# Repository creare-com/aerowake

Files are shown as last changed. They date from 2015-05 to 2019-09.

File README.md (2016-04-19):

# Aerowake

Also known as Wake Swarm, this is a project to measure air currents using a multicopter carrying an air pressure probe.

This repository hosts software to control the multicopter and its base station.

This project is a collaboration between Creare LLC and MIT.  For more information, please contact Creare and ask for Ben Cameron.  Contact information can be found [here](http://www.creare.com/about/contact.html).

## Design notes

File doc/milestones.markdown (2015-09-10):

# Software/Autopilot Mission Planning

---

## 1. System is integrated and demonstrated
In this milestone, the ground-control-pixhawk-raspberry pi-tether system is integrated and demonstrated on a real system. 

### Tasks
#### 1. Select the system configuration

~~In this task the initial hardware and interfaces are selected~~

#### 2. Integrate systems

In this task (Due 2015/9/17)

* ~~the raspberry pi can send/receive commands to/from the pixhawk at the maximum rate (10 Hz)~~
* ~~the raspberry pi can send/receive commands to/from the ground station~~
* ~~the ground station can receive telemetry/GPS information from the pixhawk~~
* the ground station can send GPS information and mission commands to the raspberry pi, and receive data packages from from the raspberry pi
* ~~the pixhawk can receive commands from the raspberry pi and send gps/telemetry information to the raspberry pi~~
* ~~the pixhawk can send telemetry/gps information to the ground station~~

#### 3. Develop autonomous mission control

In this task (Due 2015/9/24)

* A user can specify a sampling grid with various parameters
   * ~~r, $\theta$, $\phi$, maxes and mins and number of points between max and min~~
   * loiter time at points
   * travel speed between points
* The sampling grid waypoints will be generated
* The raspberry pi can take this grid and control the pixhawk to cover the gridded area flying relative to the ground-station gps coordinates
* If communication with the ground station is lost, the raspberry pi can interrupt the mission and control the pixhawk to land
   * Same thing with other critical problems (Such as low battery) -- need to define failure criteria

#### 4. Manual System Demonstration

In this task (Due 2015/09/24), it will be demonstrated that the copter can fly when manually controlled when

* the copter is untethered and the ground station is stationary
* the copter is tethered and the ground station is stationary
* the copter is tethered and the ground station is moving

#### 5. Autonomous System Demonstration

In this task (Due 2015/10/08), it will be demonstrated that the copter can fly a simple grid pattern relative to the ground station when

* the copter is untethered and the ground station is stationary
* the copter is untethered and the ground station is moving
* the copter is tethered and the ground station is stationary
* the copter is tethered and the ground station is moving

#### 6. Tether reel integration
In this task (Due 2015/10/15)

* The reel control can be controlled through the ground station
* The reel status can be sent to the raspberry pi, and the raspberry pi can ask the ground control station to reel the copter in or out
* In case of catastrophe, the reel will automatically retract to pull the copter back to landing

-----
## 2. System is optimized and stable
In this milestone, the copter-tether dynamical system is understood from energy-optimal and stability perspectives, and can be robustly controlled. 

### Tasks

#### 1. Analytically analyze the tether-copter system to determine limits of the performance envelope
In this task (Due 2015/11/10)

* Equation for the tether-copter system are developed
* The maximum tether-copter angles (both $\theta$ and $\phi$ are calculated to show where the tether reduces energy requirements

#### 2. Optimize energy performance
In this task (Due 2015/11/10)
* A function or lookup table for the optimal tether tension and copter pitch is calculated (inputs being tether length, $\theta$, and $\phi$

#### 3. Optimize stability
In this task (Due 2015/11/10)

* The best tether attachment point is determined

---
## 3. Ground Control Software is user-friendly
In this milestone, then Ground control software has an easy-to-use and robust GUI

### Tasks
#### 1. Integrate outputs received from quadcopter with GUI elements in GCS
~~In this task (Due 2015/09/17) there are new dials to show the outputs from measurements in real time~~

#### 2. Add custom mission control buttons
In this task (Due 2015/09/17), new GUI elements are added to control the mission on a high level. This includes specifying the grid, controlling the tether, ~starting and stopping the mission, emergency landing, and emergency stop~

#### 3. Validate and test GUI components with Hardware for normal usage
In this task (Due 2015/10/01), it is verified that the GUI buttons and outputs work as expected

#### 4. Test GUI elements

In this task (Due 2015/10/15), it is verified that the GUI buttons and outputs work as expected for anticipated emergency cases

----
# Other Milestones

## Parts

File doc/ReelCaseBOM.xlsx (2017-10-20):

Reel Case BOM |  | Up to date as of: | 2017-10-17
 | Brand | Part/Model # | QTY | Notes
Flight Electronics
Single-board computer |  | Raspberry Pi 3 | 1
915MHz Radio | 3DR | Pixhawk Radio Set, 915 mhz | 1
Pixhawk | 3DR | Pixhawk | 1
GPS module | 3DR |  | 1
Buzzer | 3DR |  | 1
I2C A to D converter | Adafruit | ADS1115 | 1
Power Supplies
5-12-24 Power supply | Traco Power | 495-TXL-100-0534TI | 1
48V Power supply | TKD-LAMBDA | SWS300 | 1
Case Hardware
Switch /Port mount | Digikey/Creare | HM577 HAMMOND BOX
Power switch | McMaster | 8002K82 | 1
Antenna port | Digikey | ACX1244 SMA BULKHEAD | 2
Antenna adapter | Digikey | ACX1248 SMA RPSMA SOCKET | 1
Antenna adapter | Digikey | ACX1247 SMA RPSMA SOCKET | 1
Antenna cable | Digikey | ACX1589 SMA 12" CABLE | 2
Antenna cap | Mouser | 523-8018-6174 SMA CAP | 2
Power port | Mouser | 654-MS3112E12-3P CONNECT | 1
Power cord | Digikey | MS3116F-12-35-MIL CONN | 1
Power port cap | Digikey | 1591-1044-MIL 12-3 CAP | 1
USB port | Digikey | APC 1103 USB HEADER | 1
USB port cap | Digikey | APC 1112 USB CAP | 1
USB plug | Digikey | APC 1107 USB PLUG | 1
Ethernet port | alliedelec | 70026494 AMP RJFTV21N | 1
Ethernet port cap | alliedelec | 70026506 AMP RJFTVC2N | 1
Ethernet plug | alliedelec | 70026500 AMP RJFTV6MN | 1
Exhaust fan | Sunon | GF92251B-000U-AE9 | 1
light green | McMaster | 2779K12 | 1
light blue | McMaster | 2779K2 | 1
Fuse Holder | McMaster | 7055K28 | 1
Tether pass-thru | McMaster/Creare
ANGULAR-CONTACT BALL BRNG | McMaster | 8828T216 | 1
THROUGH-WALL FITTING | McMaster | 36895K144 | 1
FOOD-GRADE DRY-RUNNING SLEEVE BRNG | McMaster | 57785K229 | 1
Motor/Reel Electronics
Motor controller | MAXON | 375711 EPOS2 70/10 | 1
Tension sensor | ELECTROMATIC | RFS150E/0200/08/3/O/4-20 | 1 | 0-200N range
Tether Encoder (Optical) | BAUMER (WALKER) | G1342A 227123 | 1
Gear/Motor/Encoder | MAXON | 136212 | 1 | 250W
Motor/Reel Mechanicals
Short Pulley Assy | Creare | 6614-010-0021 | 1
Long Pulley Assy | Creare | 6614-010-0022 | 1
Tensioner Assy | Creare | 6614-010-0030 | 1
6in Pulley | McMaster | 6245K480 | 1
Pillow Block Bearing | McMaster | 5913K610 | 2
Torque Limiter | McMaster | 6609K11 | 1 | 25 in-lbs
80/20 Frame | Creare | Custom | 1
Case
iM2620 STORM TRAK CASE | Pelican | iM2620 | 1

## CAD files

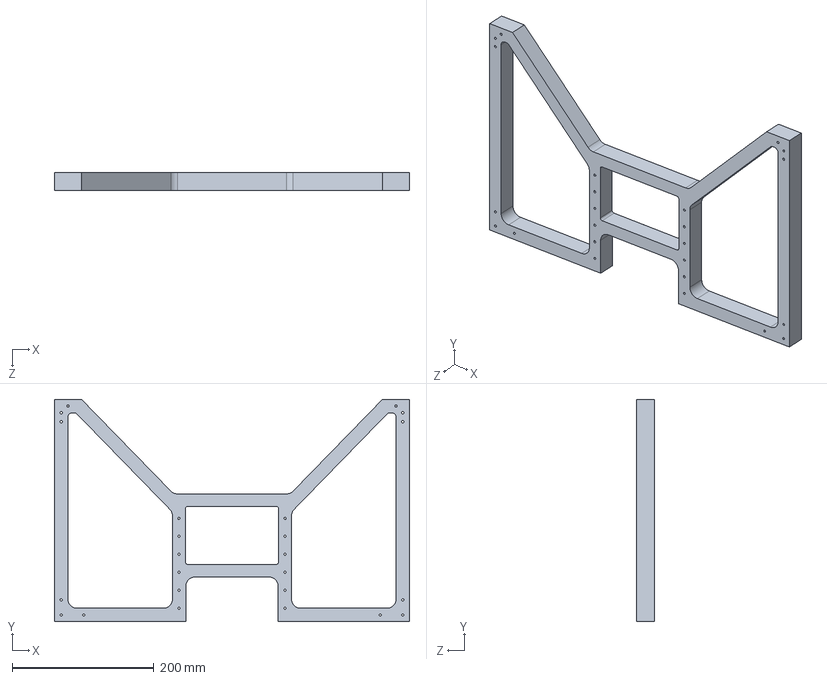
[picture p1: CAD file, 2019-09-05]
doc/design/1006614-002-0110 - Body Frame_rA.STEP
501.7 x 314.3 x 25.4 mm

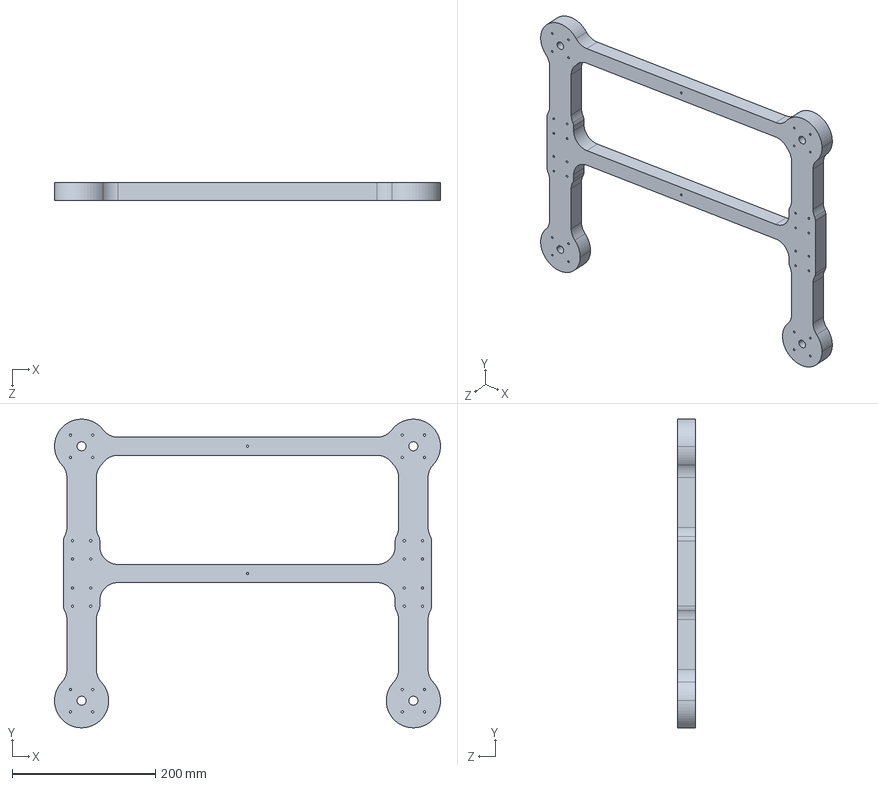
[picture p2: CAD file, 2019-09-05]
doc/design/1006614-002-0113 - Motor Mount Frame_rA.STEP
539.3 x 431.3 x 25.4 mm

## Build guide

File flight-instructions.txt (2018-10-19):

SIMPLE EXPLANATION IN ORDER

SSH into each device:
ssh odroid@192.168.1.3
ssh pi@192.168.1.6

Calibrate each pixhawk:

ODROID:
mavproxy.py --master=/dev/pixhawk,57600
accelcal
magcal start
magcal accept

RPi:
mavproxy.py --master=/dev/ttyAMA0,115200
accelcal
magcal start
magcal accept

Power cycle each pixhawk

Start flight commands:

ODROID:
sudo chmod a+rwx /dev/i2c-4
preflight.sh FILENAME

RPi:
ssg
ipython aerowake/Flight\ source/gcs/main.py FILENAME

Check on airprobe:

ODROID:
"CTRL+A,D" to detach from flight-cmd screen
"sral" to reattach to airprobe listener

Start rosbag (saving video)

ODROID:
"CTRL+A,D" to detach from airprobe listener
"ssb" to start bag screen
"rosbag record -a -x /camera/image --split --size=3000 --lz4 -o FILENAME" to start recording

Stop rosbag

ODROID:
"CTRL+C" in bag screen

Stop flight commands

ODROID:
postflight.sh

RPi:
End main.py with quit or CTRL+C

Playback rosbag

ODROID with monitor attached:
"CTRL+ALT+T" to start a terminal
roscore
"CTRL+SHIFT+O" to start a new terminal below the original
rosbag play /crearedrive/rosbag/FILENAME*
"CTRL+SHIFT+E" to start a new terminal next to the rosbag terminal
rosrun image_view image_view image:=/camera/image_raw

Logfile Storage Locations

airprobe log file: /crearedrive/airprobe-logs/FILENAME-TIME.log
uav main log file: /crearedrive/uav-logs/FILENAME-uav-TIME.log
rosbag log file: /crearedrive/rosbags/FILENAME
gcs main log file: /home/pi/logs/gcs-logs/FILENAME-gcs-TIME.log
gcs reel log file: /home/pi/logs/reel-logs/FILENAME-reel-TIME.log

################################################################################################################################################################################################################################################################################################################################################################################################################################################################################################

MORE COMPLETE EXPLANATIONS

SSH Connections

If unsure what IP address a device is on, log onto routerlogin.com (username: admin password: password) to see attached devices. IP addresses below are assigned to the WiFi chip itself, not the device. If you change WiFi chips, you will likely have a different IP from what is below.

RPi: 192.168.1.6
Yellow Hex: 192.168.1.3
FA39: 192.168.1.5

Initial Calibration

Need to calibrate camera on the drone. With the monitor attached, start roscore in one terminal, then launch the calibration method in a different terminal. Move the calibration target (extras in big MIT bin inside blue bag inside file box) around in the image until "Calibrate" lights up. Then click calibrate. It will likely take a few minutes until "Save" and "Commit" light up. Click "Save" followed by "Commit". The calibration file is created in ~/creare_ws/src/creare/params/camera_calib.yaml, even if the calibration terminal shows an error. 

roscore
<new terminal>
roslaunch creare calibrate.launch
<move calibration target in image>
<click calibrate>
<click save>
<click commit>
<CTRL+C launch terminal and roscore terminal>

Need to calibrate accelerometers and magnetometers on both pixhawks. When logged into each device below, issue the following commands to start MAVProxy, and then to begin calibration.

RPi:
mavproxy.py --master=/dev/ttyAMA0,115200

ODROID:
mavproxy.py --master=/dev/pixhawk,57600

In MAVProxy:

accelcal
Start accelcal, then follow prompts. If is hangs (doesn't go through all the prompts) and you try again and it always says calibrated, power cycle the pixhawk and complete accelcal through all of the prompts (end with "on its back"). 

magcal start
magcal accept
Start magcal, turn around in circles until it beeps confirmation, then accept once it says finished.

Pre- and Post-Flight Commands

Need to issue a number of commands in different screens (persistent SSH terminals) on the ODROID and RPi. 

ODROID:
preflight.sh FILENAME
<After flight, detach from flight-cmd screen with CTRL+A,D>
postflight.sh

I wrote shortcuts (stored in ~/creare_ws/src/aerowake/aerowake_git/preflight.sh and postflight.sh) to do so. 

The preflight shortcut will:
- start roscore in a detached screen
- start camera in a detached screen
- start flight companion in a detached screen
- start airprobe logging in a detached screen
- start airprobe checking (tail -f) in a detached screen
- reattach flight companion screen to view uav/main.py status

The postflight shortcut will:
- issue CTRL+C in all screens
- terminate all screens

RPi:
ssg
cd aerowake/Flight\ source/gcs
ipython main.py FILENAME

General Screen Commands

screen -ls
Lists all active screens.
screen -S NAME
Starts a screen with the given name.
screen -D NAME
Detaches from screen of given name.
CTRL+A,D
Detaches from current screen. Useful when a process is running on a screen and you can't type "screen -D NAME". If you press this combination in a terminal that is not a screen, it will close the terminal. 
screen -r NAME
Reattaches to screen of given name. A screen with that name must exist. 
killall screen
Terminates all active screens.

I wrote numerous shortcuts on the ODROID and RPi to quickly issue screen commands. See these commands in ~/creare_ws/src/aerowake/aerowake_git/.bash_aliases. The most useful ones are:

sls
Equivalent to "screen -ls".
skl
Equivalent to "killall screen".
srr
Equivalent to "screen -r roscore"
sry
Equivalent to "screen -r yaw-cmd". yaw-cmd is the camera start screen.
srf
Equivalent to "screen -r flight-cmd". flight-cmd is the flight companion screen.
sra
Equivalent to "screen -r airprobe". 
sral
Equivalent to "screen -r probe-check". probe-check is the "tail -f" screen.

Each ODROID Preflight Command Separately in Order

ssr (or "screen -S roscore")
roscore
CTRL+A,D
Start the roscore screen, start roscore, detach

ssy (or "screen -S yaw-cmd")
roslaunch creare yaw_commanding.launch
CTRL+A,D
Start the camera screen, start the camera, detach

ssf (or "screen -S flight-cmd")
roslaunch aerowake flight_companion.launch
CTRL+A,D
Start flight companion screen, start flight companion, detach

ssa (or "screen -S airprobe")
nice -n -10 ipython ~/creare_ws/src/aerowake/aerowake_git/Flight\ source/uav/airprobe/airprobe_main.py FILENAME
CTRL+A,D
Start airprobe screen, start airprobe with given filename, detach

ssal (or "screen -S probe-check")
tail -f /crearedrive/airprobe-logs/FILENAME*
CTRL+A,D
Start probe-check screen, echo live update tail of log file to screen, detach

srf (or "screen -r flight-cmd")
Reattach to flight-cmd screen to view uav/main.py status

Common Problems

If the airprobe won't start, you may not have set the i2c permissions. 
sudo chmod a+rwx /dev/i2c-4

Most other problems occur because you don't have the crearedrive plugged in, or the crearedrive you have plugged in doesn't have the correct directories. Each crearedrive automatically mounts to /crearedrive. Each crearedrive needs the following directories:
/crearedrive/airprobe-logs
/crearedrive/camera
/crearedrive/rosbags
/crearedrive/uav-logs

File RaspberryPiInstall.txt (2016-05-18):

Raspberry Pi Installation Guide
=================================
=================================

This can be slightly different depending on which Raspberry Pi (2 or 3). Differences should be noted. 

Setup of Raspberry Pi
=====================
-Install Basic Raspian via NOOBS (follow any online tutorial -- I am using NOOBS v1.4.1)
	-While it is installing, select Language = English (US) and Keyboard = (us)
-Default login is (pi), password is (raspberry)
-Notes:
	-To start the Raspberry Pi desktop, type $ startx
	-From the desktop, there is a wifi utility 
	- '$ [command]' will be terminal commands in this document
-Enter Raspberry Pi Config -- This often pops up when you first boot the RaspPi after installing the operating system. 
	$ sudo raspi-config
-Select '8. Advanced Options' and change:
	-A1 Overscan = Disable
	-A4 SSH = Enable
	-A7 I2C = Enable
	-A8 Serial = Disable
-Select Finish, reboot. 
-Setup Internet on the Raspberry Pi. (follow any online tutorial)
	-I used Wifi TP-Link WN722N, however there is a whole list of adapters recommended for the Raspberry Pi.
	-Ethernet should work fine. 
-Update the Raspberry Pi Software
	$ sudo apt-get update 
	$ sudo apt-get upgrade 
	$ sudo apt-get install git

Installation of Github Repository
====================================	
-Clone the repository
	$ git clone https:/github.com/creare-com/aerowake
	-This will probably require an authorized account. 

Serial Communication using GPIO pins
====================================
 -Run serial_enable_rasppi.sh in the aerowake repository
 	$ sudo ./serial_enable_rasppi.sh
 -The following can be used to change the baudrate, but are not necessary. 
 	for RaspPi 3:
 	$ sudo stty -F /dev/ttyS0 115200 
 	for RaspPi 2:
 	$ sudo stty -F /dev/ttyAMA0 115200

Installation of Dronekit and Mavproxy
=====================================
-Install packages 
	$ sudo apt-get install screen python-wxgtk2.8 python-matplotlib python-opencv python-pip python-numpy python-dev python-serial python-pyparsing 
	$ sudo pip install pymavlink
	$ sudo pip install mavproxy
	$ sudo ppip install dronekit

Testing of Pixhawk Connections
=====================================
	
-Use Mavproxy to ensure the pixhawk connections work. Start with the GCS pixhawk. Plug the Pixhawk Telemetry Radio into the Raspberry Pi. Set up the telemetry radios using a normal computer with Mission Planner, and confirm they work. 
	-Power the GCS Pixhawk on. 
	-Enter the following command  
	$ mavproxy.py --master=/dev/ttyUSB0 --baudrate 57600
	-You should see it initialize and say the firmware version**
	-When mavproxy is running, there are a list of commands that you can enter -- view all by typing help
	-For this document, Mavproxy commands will be shown as MAV> [command], however MAV will be the flight mode the vehicle is in, such as AUTO or MANUAL or ALTHOLD. 
	-If the pixhawk does not connect, there is an issue with the telemetry radio system. Most likely the issue is with the telemetry radios not being on the same channel. 
-Ctrl-C to exit Mavproxy. 
-Next attempt to connect to the UAV pixhawk.
 	-Ensure that the raspberry pi's GPIO pins are connected to the pixhawk's telemetry 1 port, and that the pixhawk is configured to use 115200 baud on that telemetry port. This is parameter SERIAL1_BAUD, and will have to be set using Mission Planner on a normal computer. 
 	-For the Raspberry Pi 2:
	$ mavproxy.py --master=/dev/ttyAMA0 --baudrate 115200
 	-For the Raspberry Pi 3:
 	$ mavproxy.py --master=/dev/ttyS0 --baudrate 115200
 	-If mavproxy cannot connect, it is most likely an issue with the Raspberry Pi's serial port on the GPIO. This can have to do with incorrect baud rates, the user not being on the dialout group, or the raspberry pi configuring the serial port for another function upon startup. The serial_enable_rasppi.sh script will hopefully fix these problems, but the Raspbery Pi 3 is known to be problematic with the serial port on the GPIO. 

Wiring Instructions
===================
-The Raspberry Pi 2 needs 5 volts @ up to 1A. Realistic current draw is ~.5A, but USB devices will draw more, so a large safety margin is good. 
	-I used 3 7805 5v Linear regulators in parallel (they got hot during operation)
	-Would recommend a high-power, high quality switching regulator such as this: http://www.amazon.com/Castle-Creations-Bec-Switching-Regulator/dp/B000MXAR12
	-This should be fed from a 12volt power source (3 cell LiPo) onboard the UAV. This battery hot-swappable, as we dont want to keep shutting down the raspberry pi.

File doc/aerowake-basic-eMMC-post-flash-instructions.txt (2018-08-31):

#---------------
# Setup Steps After Flashing aerowakebasic Image (Send questions to draper@mit.edu)
#---------------

Initially the ODROID will not boot due to having no hard disk space. To get it to boot, complete the following:

1. Press CTRL + ALT + F1 to enter a terminal
2. Login by typing odroid as the login and then again as the password
3. Start the ODROID Utility by typing "sudo odroid-utility.sh"
4. Within ODROID Utility, complete "4 Resize your root partition"
5. Within ODROID Utility, complete "7 Change Hostname", and change the hostname as desired -- DO NOT USE UNDERSCORES IN HOSTNAME
6. Once completed, reboot the ODROID using "sudo reboot now"

Once the ODROID boots to the desktop, complete the following:

1. Ensure you are connected to the internet
2. Start ODROID UTILITY again, and select "2 Update your Kernel/Firmware" then complete "1 Update Kernel"
3. Reboot using "sudo reboot now"
4. Then issue the following commands in order:
sudo apt-get update && sudo apt-get upgrade
cd ~/creare_ws/src
git clone https://Brndn004@bitbucket.org/Brndn004/creare.git
catkin_create_package aerowake
cd ~/creare_ws
catkin_make
cd ~/creare_ws/src/aerowake
git clone https://github.com/creare-com/aerowake.git aerowake_git
cd aerowake_git
git checkout may-2018-flight-testing
cd ~/creare_ws
catkin_make
sudo ln -s ~/creare_ws/src/aerowake/aerowake_git/Flight\ source/FA39.rules /etc/udev/rules.d/
sudo udevadm control --reload-rules && sudo udevadm trigger
git config --global user.email "Your Email"
git config --global user.name "Your Name"
mkdir ~/.ros/aerowake-logs
sudo reboot now

#---------------
# Programs Installed on this Installation Different from Base Ubuntu Image 
#---------------

- ROS Indigo
- ROS image_view package for when monitor attached to odroid
- ROS Catkin Workspace in ~/creare_ws/
- ROS Pointgrey Camera Driver built from source in ~/creare_ws/src/
- terminator (CTRL + ALT + T to open)
- pip
- Dronekit
- MAVProxy

#---------------
# Exact steps taken to set up this installation for Creare Aerowake
#---------------

<set system to allow updates from main, universe, restricted, and multiverse)
sudo apt-get update && sudo apt-get upgrade
sudo apt-get install terminator
<install ros by following directions at wiki.ros.org/indigo/installation/Ubuntu>
<set up catkin workspace in the ~/creare_ws/ directory by following directions at wiki.ros.org/ROS/Tutorials/InstallingandConfiguringROSEnvironment#Create_a_ROS_Workspace>
sudo apt-get install ros-indigo-image-view
sudo apt-get install python-rosinstall
cd ~/creare_ws/src
git clone https://github.com/ros-drivers/pointgrey_camera_driver.git
rosdep install --from-paths /path/to/your/catkin_ws/src --ignore-src
cd ~/creare_ws
catkin_make
<create /etc/udev/rules.d/40-pgr-custom.rules and paste inside:>
	SUBSYSTEM=="usb", ATTRS{idVendor}=="1e10", ATTRS{idProduct}=="3300", GROUP=="plugdev", SYMLINK+="firefly", MODE:="0666"
sudo service udev restart
sudo apt-get install libtcmalloc-minimal4
echo "export LD_PRELOAD=\"/usr/lib/libtcmalloc_minimal.so.4\"" >> ~/.bashrc
sudo apt-get install python-pip
sudo pip install dronekit
sudo pip install MAVProxy
sudo nano /usr/local/lib/python2.7/dist-packages/dronekit/__init__.py
<search for "timeout = kwargs" and change value from 30 to 180>
<change hostname in ODROID Utility -- DO NOT USE UNDERSCORES>
sudo reboot now

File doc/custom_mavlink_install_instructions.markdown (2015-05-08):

# Installing custom MAVLINK message to be used by the GCS and Raspberry pi
These custom messages are specified at the bottom of the: third_party/mavlink/pymavlink/dialects/v10/gcs_pixhawk.xml file

## Removing existing pymavlink installations
From commandline issue
```bash
sudo pip uninstall pymavlink
``` 

## Installing pymavlink from source
From commandline issue the following commands:
```bash
cd ~
cd aerowake-mit/third_party/mavlink/pymavlink
sudo python setup.py install
```

## Editing the messages
Simply edit the file mentioned above with new message or parameters, and then re-run `setup.py install`

## Notes
* This custom version of pymavlink has to be installed on both the GCS and the onboard PI to work
   * Hence why I included it in the repository
   * I also kept the .git folder so that we could potentially pull upstream changes (bugfixes) from the pymavlink project
* If you don't want to wait for all the mavlink protocols to be built use: 
```bash
sudo su
export NOGEN=0
setup.py install
exit
```

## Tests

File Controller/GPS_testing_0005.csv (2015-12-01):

log N | timestamp | roll | pitch | yaw | throttle | vox | voy | voz | vth | vphi | vr | airspd | lat | lon | alt | th | phi | goal_th | goal_phi | fx | fy | fz | fix | fiy | fiz | p | r | thr | yw | s_lat | s_lon | t_dist | s_alt | s_head | s_vel_x | s_vel_y | s_vel_z | v_rel_x | v_rel_y
1 | 15:09:44 | -0.01484086 | -0.06830316 | 52.36049314 | 1.23000000 | -0.47000000 | -0.39000000 | 0.47000000 | -0.53849802 | 0.47000000 | -0.28813170 | 0.00000000 | 1.00000000 | 1.00000000 | 0.00000000 | 138.46424372 | 0.00000000 | 0.00000000 | 20.00000000 | -3.74271029 | 3.31543658 | 20.94435000 | 3.28138291 | 3.70426798 | 0.71479013 | 1486.00000000 | 1300.00000000 | 1227.00000000 | 1537.00000000 | 42.35854040 | -71.09724260 | 8471102.97667107 | 0.00000000 | 60.00000000 | 0.00000000 | 0.00000000 | 0.00000000 | 0.57274991 | 0.21203194
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

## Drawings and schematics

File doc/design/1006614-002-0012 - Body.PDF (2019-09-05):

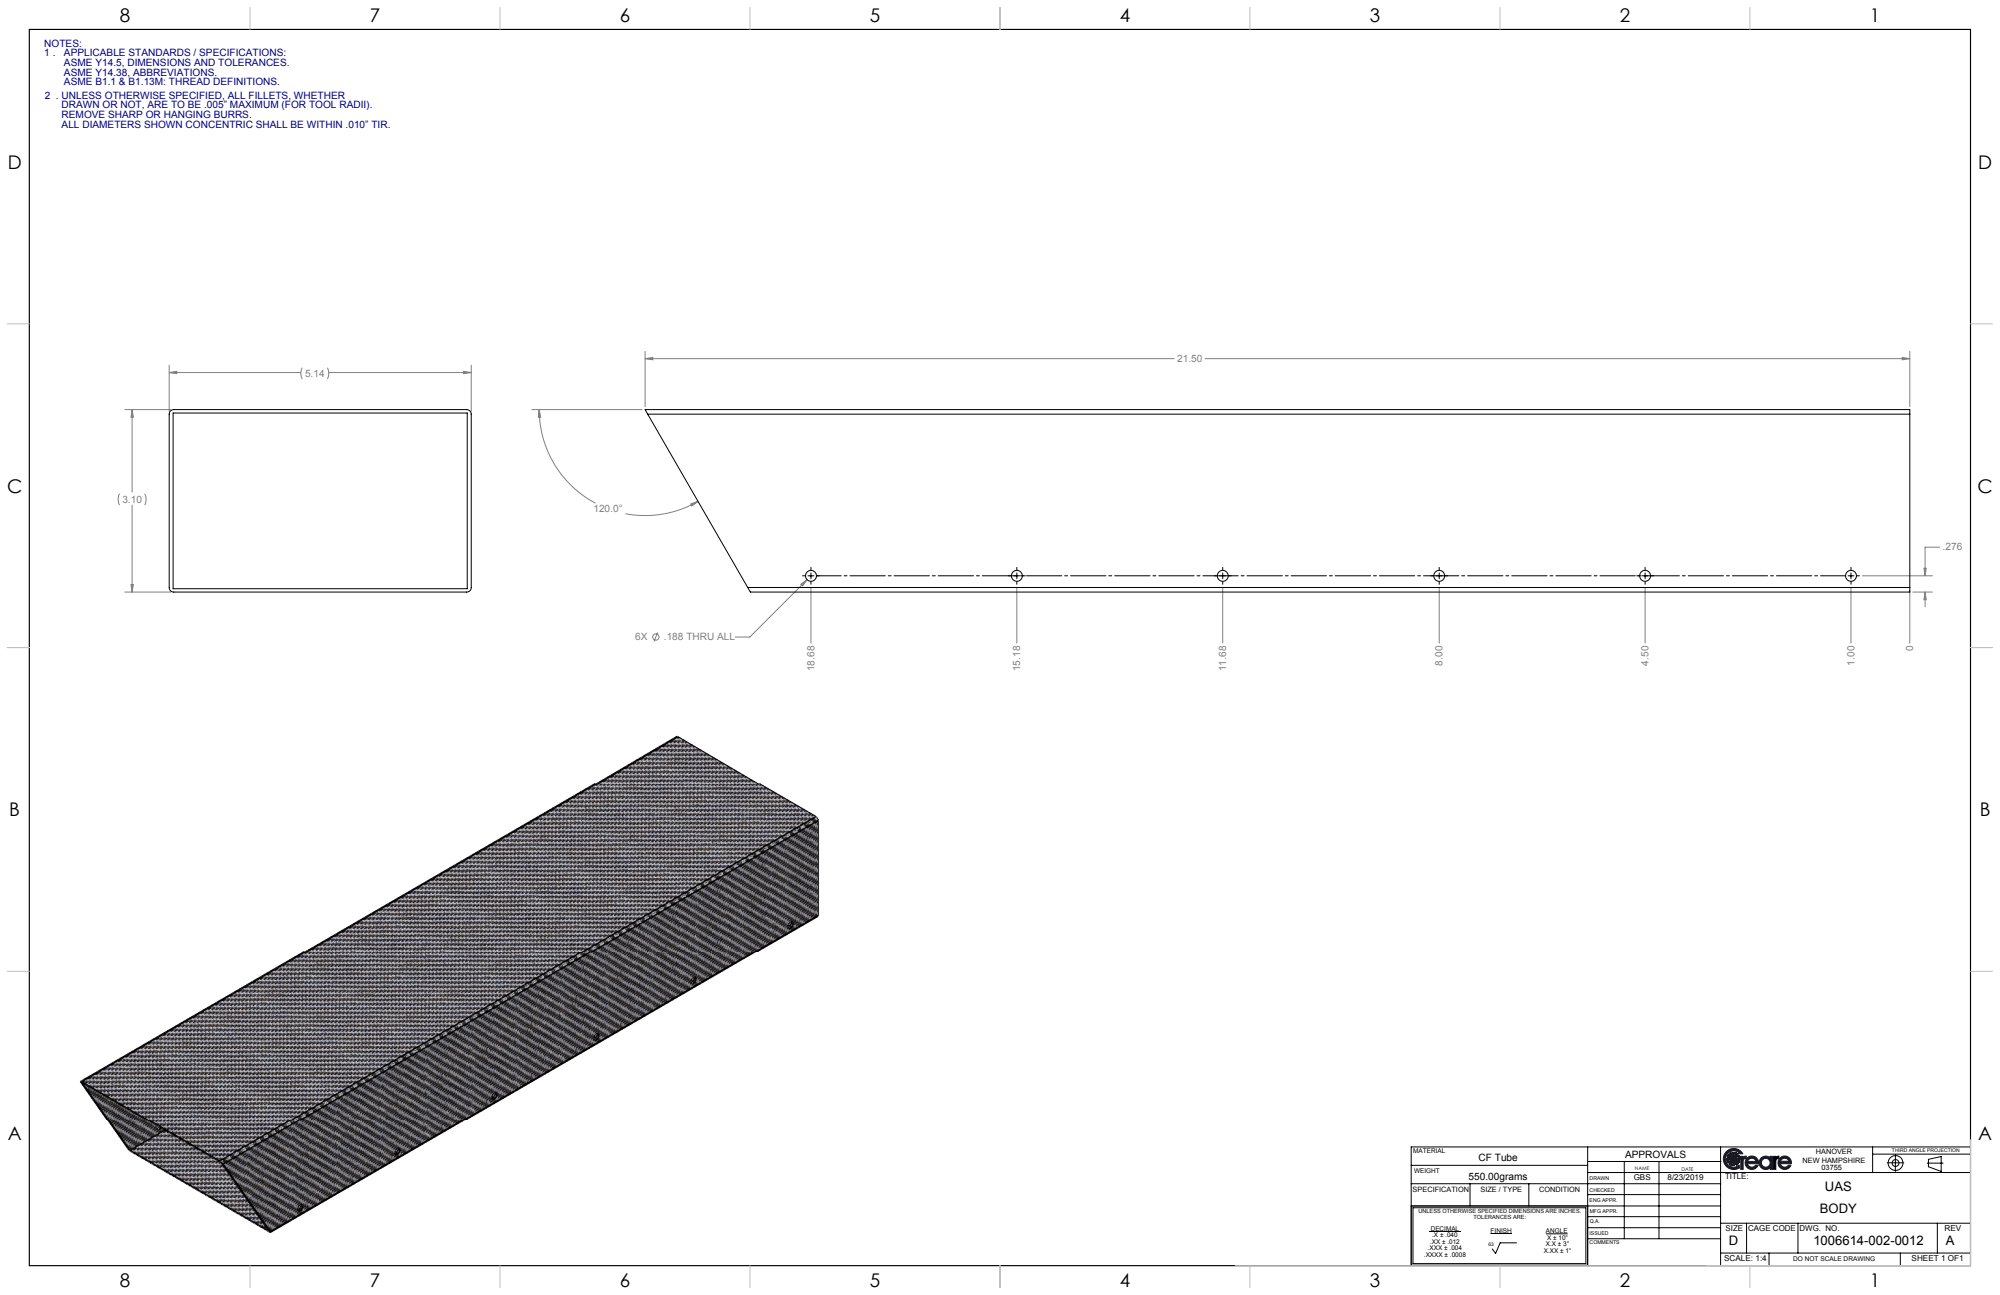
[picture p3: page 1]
TOLERANCES ARE:; .X ± .040 .XX ± .012 .XXX ± .004 .XXXX ± .0008; .188 THRU ALL; CF Tube; SCALE: 1:4; SHEET 1 OF1; SPECIFICATION SIZE / TYPE; CONDITION; NEW HAMPSHIRE APPROVALS; HANOVER; CAGE CODE; ENG APPR.; MFG APPR.; SIZE; DWG. NO.

NOTES:
1 . APPLICABLE STANDARDS / SPECIFICATIONS:
ASME Y14.5, DIMENSIONS AND TOLERANCES.
ASME Y14.38, ABBREVIATIONS.
ASME B1.1 & B1.13M: THREAD DEFINITIONS.
2 . UNLESS OTHERWISE SPECIFIED, ALL FILLETS, WHETHER
DRAWN OR NOT, ARE TO BE .005” MAXIMUM (FOR TOOL RADII).
REMOVE SHARP OR HANGING BURRS.
ALL DIAMETERS SHOWN CONCENTRIC SHALL BE WITHIN .010” TIR.

THIRD ANGLE PROJECTION

UNLESS OTHERWISE SPECIFIED DIMENSIONS ARE INCHES.

DO NOT SCALE DRAWING

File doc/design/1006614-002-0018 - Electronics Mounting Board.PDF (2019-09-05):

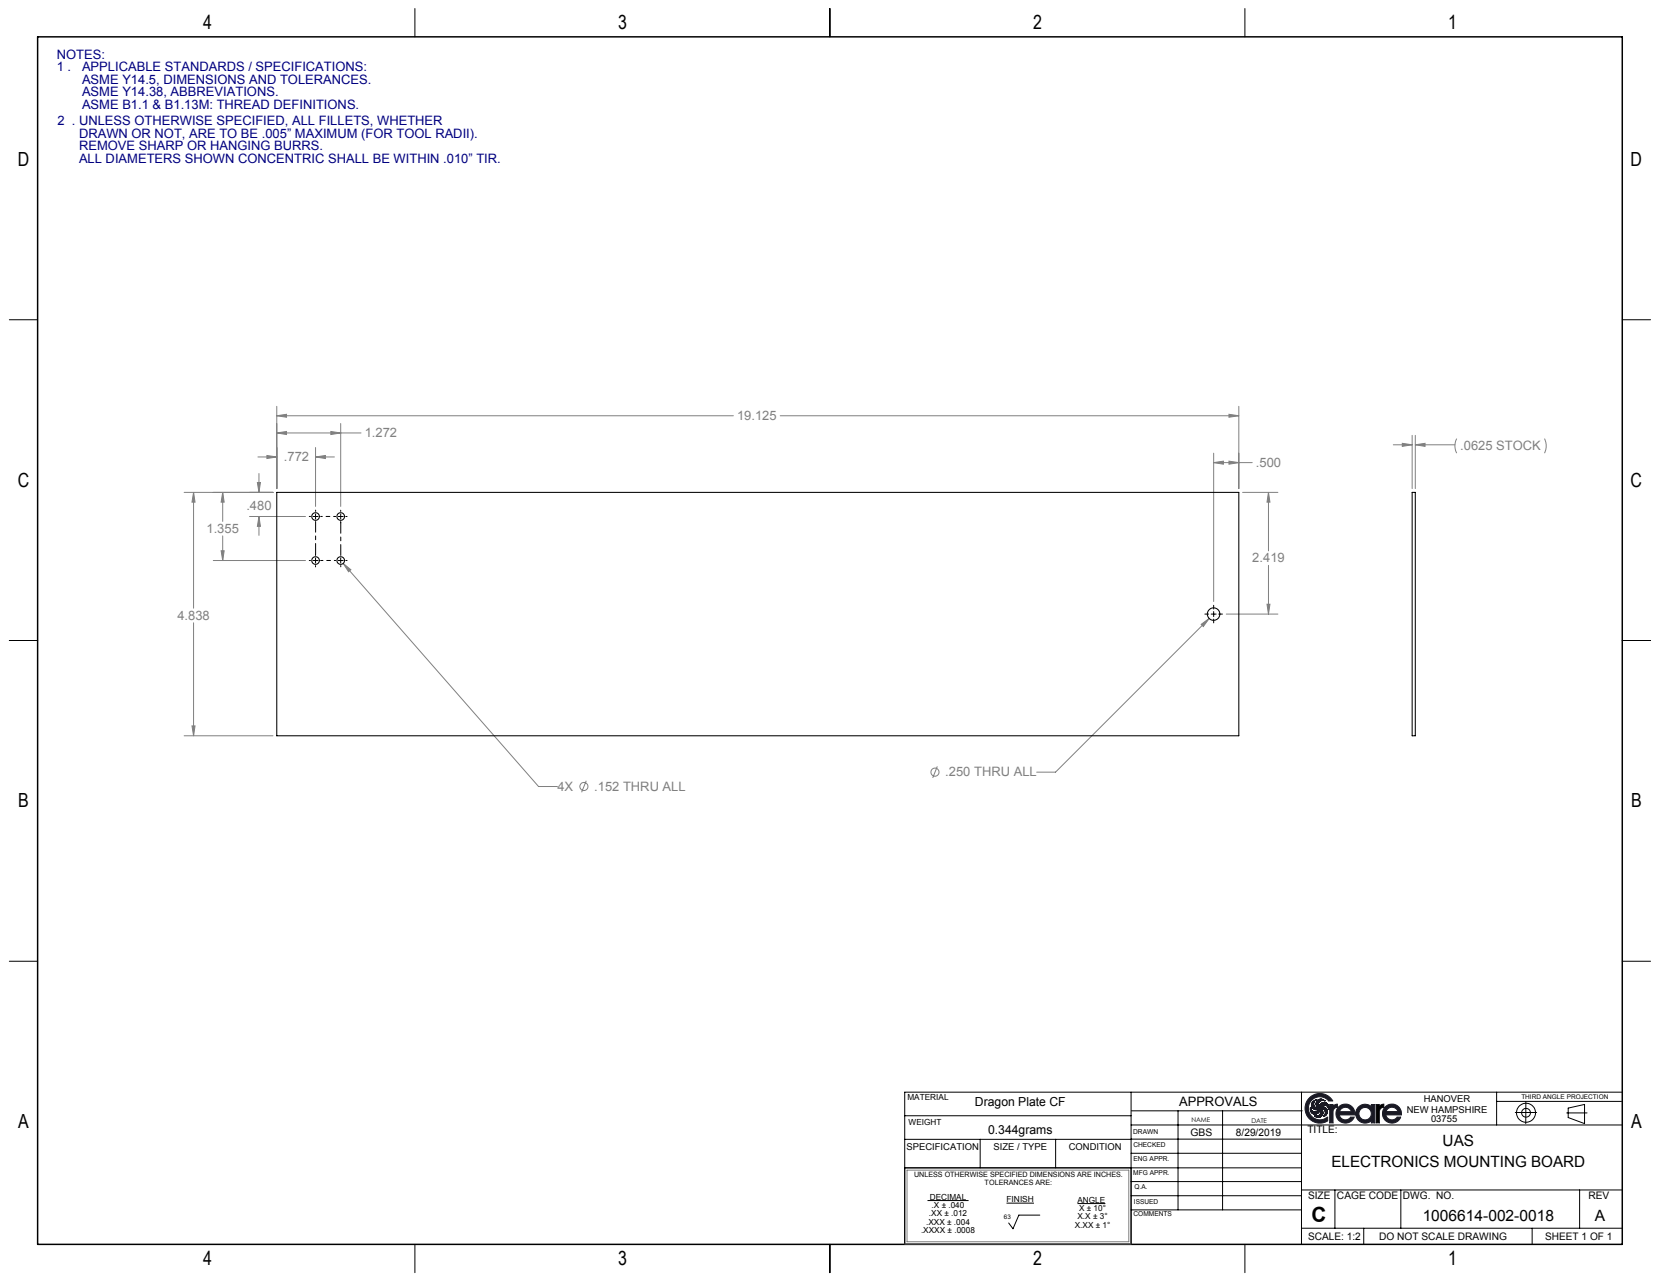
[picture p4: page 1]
TOLERANCES ARE:; .X ± .040 .XX ± .012 .XXX ± .004 .XXXX ± .0008; .152 THRU ALL; .250 THRU ALL; .0625 STOCK; ELECTRONICS MOUNTING BOARD; DO NOT SCALE DRAWING; SHEET 1 OF 1; SCALE: 1:2; DWG. NO.; REV; MFG APPR.; ENG APPR.; CAGE CODE; NEW HAMPSHIRE; SPECIFICATION SIZE / TYPE; CONDITION; UAS

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

ALL DIAMETERS SHOWN CONCENTRIC SHALL BE WITHIN .010” TIR.

THIRD ANGLE PROJECTION

Dragon Plate CF
0.344grams

UNLESS OTHERWISE SPECIFIED DIMENSIONS ARE INCHES.

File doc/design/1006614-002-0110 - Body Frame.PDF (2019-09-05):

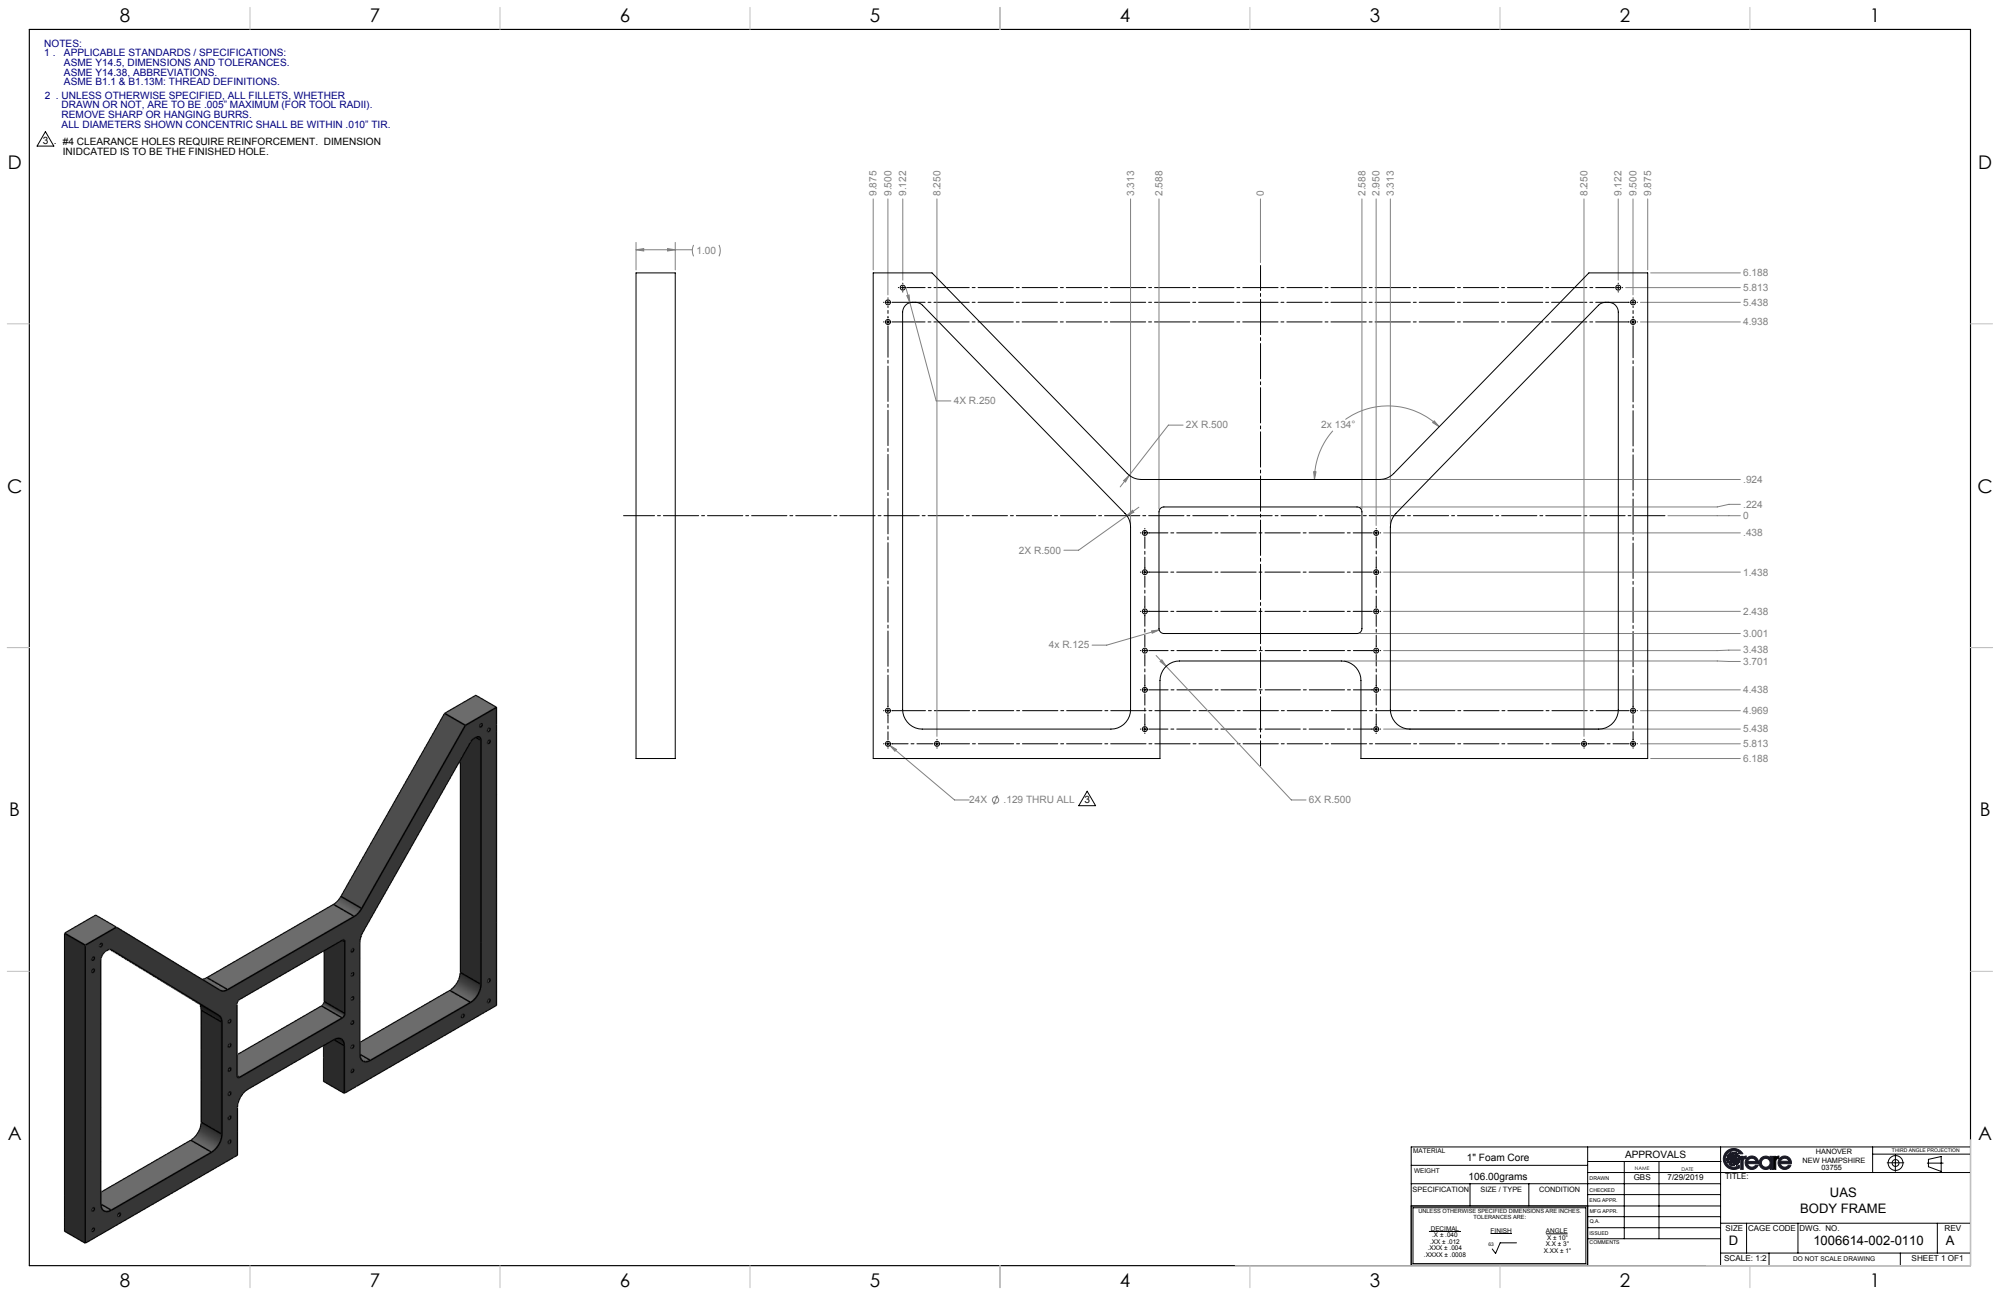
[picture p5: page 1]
TOLERANCES ARE:; .X ± .040 .XX ± .012 .XXX ± .004 .XXXX ± .0008; .129 THRU ALL; 1" Foam Core; SCALE: 1:2; SHEET 1 OF1; SPECIFICATION SIZE / TYPE; CONDITION; NEW HAMPSHIRE APPROVALS; HANOVER; CAGE CODE; ENG APPR.; MFG APPR.; SIZE; DWG. NO.; BODY FRAME

NOTES:
1 . APPLICABLE STANDARDS / SPECIFICATIONS:
ASME Y14.5, DIMENSIONS AND TOLERANCES.
ASME Y14.38, ABBREVIATIONS.
ASME B1.1 & B1.13M: THREAD DEFINITIONS.
2 . UNLESS OTHERWISE SPECIFIED, ALL FILLETS, WHETHER
DRAWN OR NOT, ARE TO BE .005” MAXIMUM (FOR TOOL RADII).
REMOVE SHARP OR HANGING BURRS.
ALL DIAMETERS SHOWN CONCENTRIC SHALL BE WITHIN .010” TIR.
#4 CLEARANCE HOLES REQUIRE REINFORCEMENT. DIMENSION
INIDCATED IS TO BE THE FINISHED HOLE.

THIRD ANGLE PROJECTION

UNLESS OTHERWISE SPECIFIED DIMENSIONS ARE INCHES.

DO NOT SCALE DRAWING

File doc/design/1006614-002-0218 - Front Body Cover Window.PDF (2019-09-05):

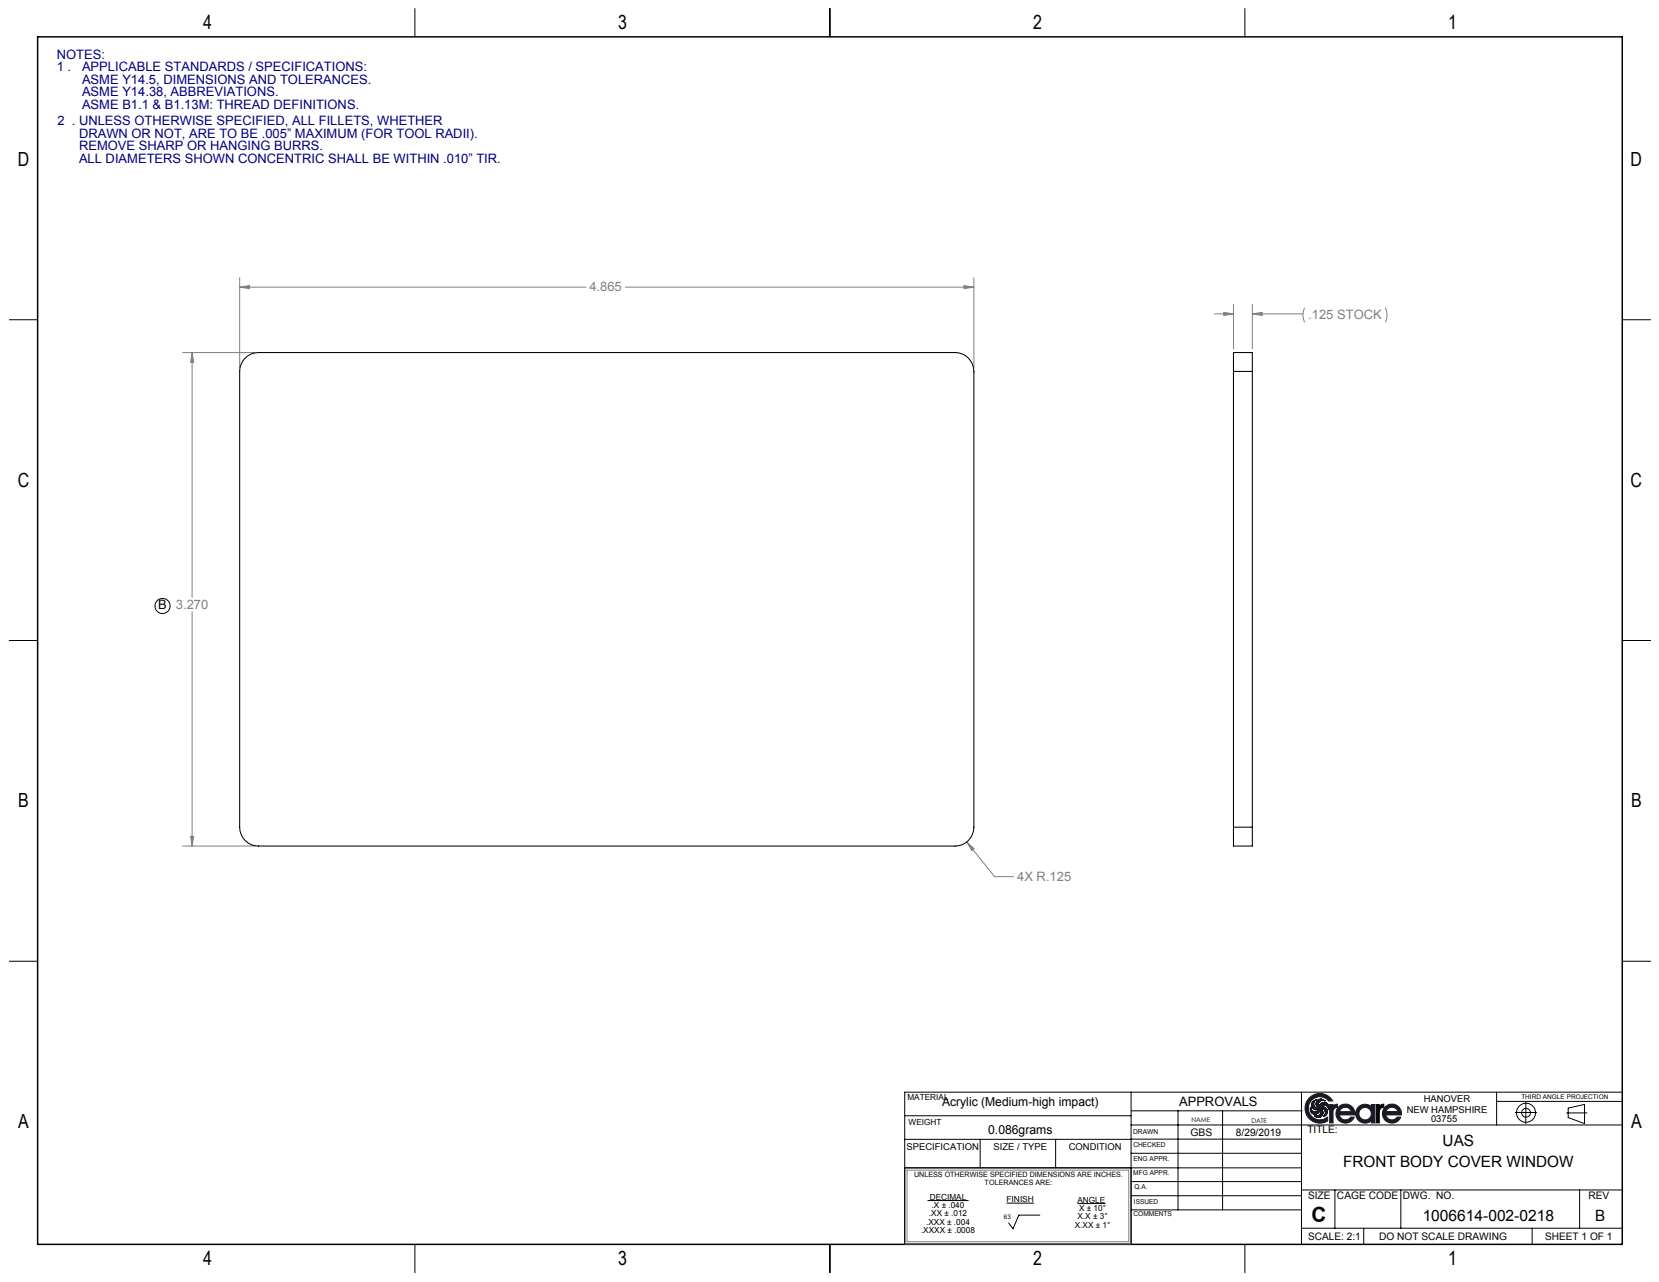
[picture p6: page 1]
TOLERANCES ARE:; .X ± .040 .XX ± .012 .XXX ± .004 .XXXX ± .0008; .125 STOCK; DO NOT SCALE DRAWING; SHEET 1 OF 1; SCALE: 2:1; DWG. NO.; REV; MFG APPR.; ENG APPR.; CAGE CODE; NEW HAMPSHIRE; SPECIFICATION SIZE / TYPE; CONDITION; UAS

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

ALL DIAMETERS SHOWN CONCENTRIC SHALL BE WITHIN .010” TIR.

MATERIAL
Acrylic (Medium-high impact)
0.086grams

THIRD ANGLE PROJECTION

TITLE:
FRONT BODY COVER WINDOW

UNLESS OTHERWISE SPECIFIED DIMENSIONS ARE INCHES.

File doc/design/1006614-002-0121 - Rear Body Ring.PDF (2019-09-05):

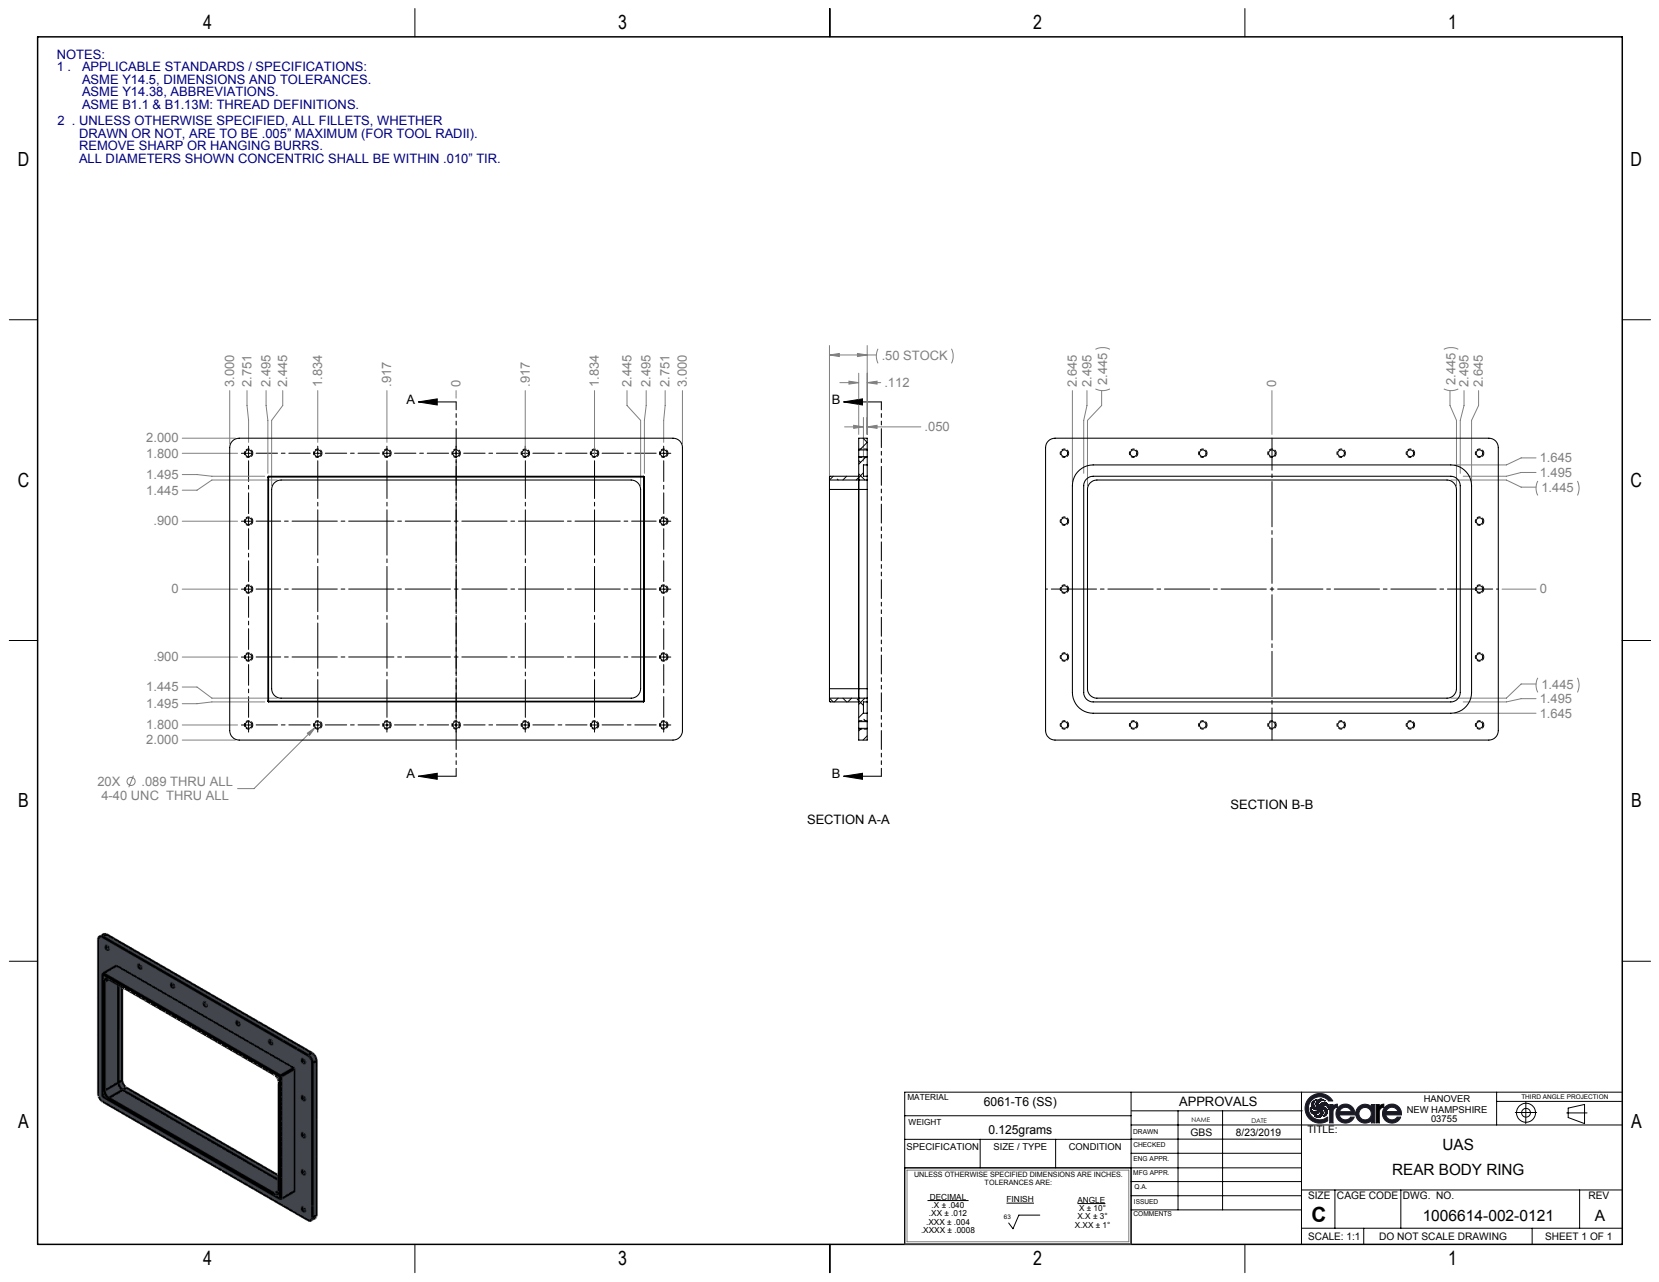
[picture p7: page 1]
TOLERANCES ARE:; .X ± .040 .XX ± .012 .XXX ± .004 .XXXX ± .0008; .089 THRU ALL; .50 STOCK; SECTION A-A; SECTION B-B; REAR BODY RING; DO NOT SCALE DRAWING; SHEET 1 OF 1; SCALE: 1:1; DWG. NO.; REV; MFG APPR.; ENG APPR.; CAGE CODE; NEW HAMPSHIRE; SPECIFICATION SIZE / TYPE; CONDITION

NOTES:
1 . APPLICABLE STANDARDS / SPECIFICATIONS:
ASME Y14.5, DIMENSIONS AND TOLERANCES.
ASME Y14.38, ABBREVIATIONS.
ASME B1.1 & B1.13M: THREAD DEFINITIONS.
2 . UNLESS OTHERWISE SPECIFIED, ALL FILLETS, WHETHER
DRAWN OR NOT, ARE TO BE .005” MAXIMUM (FOR TOOL RADII).
REMOVE SHARP OR HANGING BURRS.
4-40 UNC THRU ALL 3.000

ALL DIAMETERS SHOWN CONCENTRIC SHALL BE WITHIN .010” TIR.

THIRD ANGLE PROJECTION

UNLESS OTHERWISE SPECIFIED DIMENSIONS ARE INCHES.

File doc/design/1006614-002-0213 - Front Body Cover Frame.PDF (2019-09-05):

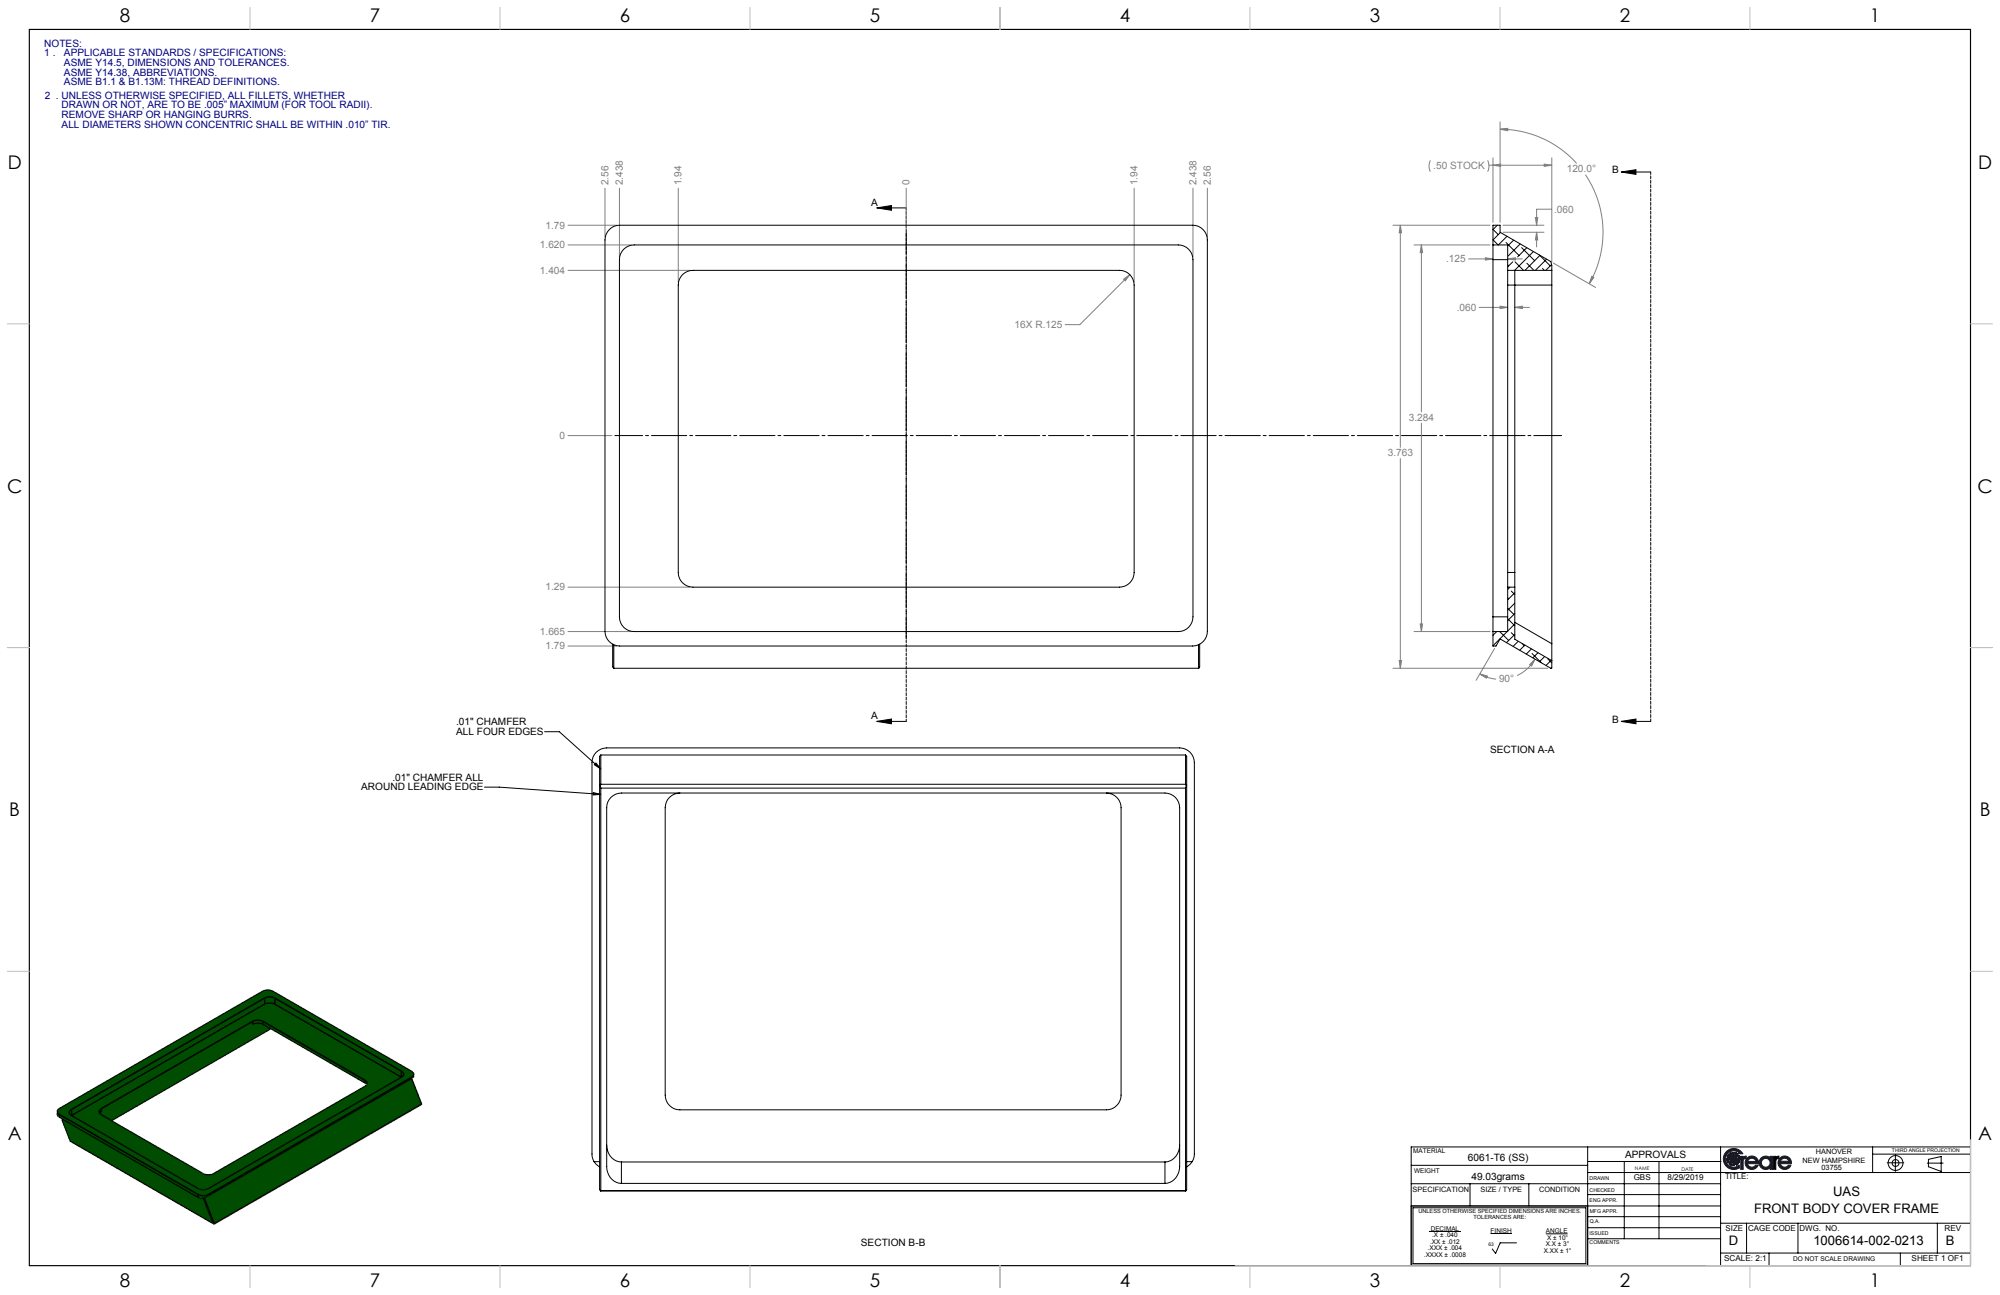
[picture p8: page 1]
TOLERANCES ARE:; .X ± .040 .XX ± .012 .XXX ± .004 .XXXX ± .0008; .50 STOCK; SECTION A-A; SECTION B-B; SCALE: 2:1; SHEET 1 OF1; SPECIFICATION SIZE / TYPE; CONDITION; NEW HAMPSHIRE APPROVALS; HANOVER; CAGE CODE; ENG APPR.; MFG APPR.; SIZE; DWG. NO.

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

.01" CHAMFER
ALL FOUR EDGES

.01" CHAMFER ALL
AROUND LEADING EDGE

THIRD ANGLE PROJECTION

TITLE:
FRONT BODY COVER FRAME

UNLESS OTHERWISE SPECIFIED DIMENSIONS ARE INCHES.

DO NOT SCALE DRAWING

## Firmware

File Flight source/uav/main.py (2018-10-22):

#!/usr/bin/env python2

# Import necessary items from parent directory, then undo changes to path
# Required for controlling the UAV
from inspect import getsourcefile
import os.path as path, sys
current_dir = path.dirname(path.abspath(getsourcefile(lambda:0)))
sys.path.insert(0, current_dir[:current_dir.rfind(path.sep)])
from helper_functions import arm_vehicle, condition_yaw, disarm_vehicle, emergency_stop, get_bearing, get_distance_metres, get_home_location, get_location_metres, goto, goto_position_target_local_ned, goto_reference, land, send_global_velocity, send_ned_velocity, set_roi, takeoff
from rotate_mission import rotate
import base_mission
sys.path.pop(0)

# Required for starting the rosbag in a really ugly way
import shlex
import subprocess

# Required for the vision-based yaw system
import rospy
from std_msgs.msg import Int16

# Required for controlling the UAV
import logging
import numpy as np
import time
from dronekit import connect, VehicleMode, LocationGlobalRelative, LocationGlobal, Command

# Required for logging
import os.path

#-------------------------------------------------------------------------------
#
# Define ROS Node for Flight
#
#-------------------------------------------------------------------------------

class DroneCommanderNode(object):
	'''
	This class will communicate with the Pixhawks on the GCS and UAV. It will then generate MAVLink commands to send to the UAV Pixhawk that will control the UAV.

	Most commands are generated based upon what the GCS tells the UAV to do. The UAV reads a GCS parameter, the value of which corresponds to a particular action.

	The UAV also obtains commands from the /yaw_deg ROS topic. This topic contains an integer (Int16) value in degrees corresponding to the desired yaw of the UAV. A positive value indicates CCW yaw of the specified magnitude, while a negative value indicates CW yaw.
	'''

	def __init__(self,uav_handle,gcs_handle,logger_name,bagfile):
		# Initialize private variables
		self.__yaw_cmd = 0 # [deg]
		self.__bagfile = bagfile

		# Initialize other variables
		uav = uav_handle
		gcs = gcs_handle
		logger = logging.getLogger(logger_name)

		# Subscribe to topic that reports yaw commands
		self.sub_yaw_deg = rospy.Subscriber("yaw_deg",Int16,self.cbYawDeg)

		# Extract mission and define a local version called uav_mission
		orig_mission = [base_mission.wp_N, base_mission.wp_E, base_mission.wp_D]
		num_wp = base_mission.num_wp
		alt_takeoff = base_mission.alt_takeoff
		wp_offset = base_mission.wp_offset

		# Define parameters to use
		cmd_param = 'PIVOT_TURN_ANGLE'
		ack_param = 'ACRO_TURN_RATE'
		bearing_param = 'RNGFND_TURN_ANGL'

		#---------------------------------------------------------------------------
		#
		# Control Code
		#
		#---------------------------------------------------------------------------

		#------------------------------------
		# Control
		#------------------------------------

		'''
		This while loop performs the following functions:
			- read GCS position
			- read GCS parameter value of PIVOT_TURN_ANGLE to determine next UAV action
			- perform an action based upon the GCS parameter value

		The parameter values corresponding actions to be performed are:
			100     UAV will stop listening to these commands
							UAV will either follow prev command, or do nothing if no command sent yet
			101     UAV will begin listening to these commands
			102     UAV will clear its current waypoint
			359     UAV will arm
			358     UAV will disarm
			357     UAV will takeoff to a pre-programmed height
			356     UAV will land according to its landing protocol
			355	UAV will rotate to bearing given by parameter RNGFND_TURN_ANGL
			300	Reserved for empty resetting ack_param so that all ack's are received
			0+      UAV will navigate to the waypoint at the index specified
							The acceptable waypoint indices are 0 through num_wp - 1
		'''

		# Ensure that at startup the UAV will not be tracking any waypoint
		current_wp = None

		# Ensure that at startup the UAV will not be listening
		gcs.parameters[cmd_param] = 100

		# We start with a 0 rotation on the mission to match what we have on the gcs
		gcs.parameters[bearing_param] = 0

		# Set UAV WPNAV params
		# NOTE: An arducopter bug does not let WPNAV_SPEED increase beyond its initial setting. However, it can decrease below its initial setting. For this reason, we initially set WPNAV_SPEED to the max we ever expect to desire. We then change it to a reasonable value after taking off. https://github.com/ArduPilot/ardupilot/issues/6711
		wpnav_speed_max = 1000
		uav.parameters['WPNAV_RADIUS'] = 100 # 10-1000 by 1 [cm]
		uav.parameters['WPNAV_ACCEL'] = 200 # 50-500 by 10 [cm/s/s]
		uav.parameters['WPNAV_SPEED'] = wpnav_speed_max # 20-2000 by 50 [cm/s]
		# uav.groundspeed = 5 # [m/s]

		logger.debug('WPNAV_ACCEL,%s' %(uav.parameters['WPNAV_ACCEL']))
		logger.debug('WPNAV_SPEED,%s' %(uav.parameters['WPNAV_SPEED']))

		command = 100 # This varibale is an echo for the variable param in order to disallow repeated commands
		i = 0
		in_the_air = False
		listening = False
		continue_loop = True
		bagging = False
		while continue_loop and not rospy.is_shutdown():
			param = gcs.parameters[cmd_param]
			gcs.parameters[ack_param] = param # Acknowledge
			gcsLoc = gcs.location.global_frame
			uavLoc = uav.location.global_frame
			logger.debug('gcsLoc,%s', gcsLoc)
			logger.debug('uavLoc,%s', uavLoc)

			print uav.battery

			'''
			The variable 'command' is what controls the drone. It is only updated when a valid and non-repeated param value is set. This ensures that the UAV does not continue commanding the same thing over and over.

			The 'command' variable can only be set while 'listening' is True. If the UAV is not listening to the GCS, then it will follow the most recent 'command' variable.

			It is occasionally desireable for waypoint commands to be repeated, so waypoint commands are handled slightly differently.

			The parameter for 'stop listening' will be immediately passed through since repeated 'stop listening' commands are also occasionally desired.
			'''

			if listening:
				logger.info('Listening')
				if param == 100:
					logger.info('Got stop listening command')
					listening = False
				else:
					if param == 102 and not command == param:
						logger.info('Got clear waypoint command')
						command = param
					elif param == 359 and not command == param:
						logger.info('Got arm command')
						command = param
					elif param == 358 and not command == param:
						logger.info('Got disarm command')
						command = param
					elif param == 357 and not command == param:
						logger.info('Got takeoff command')
						command = param
					elif param == 356 and not command == param:
						logger.info('Got land command')
						command = param
					elif param == 355 and not command == param:
						logger.info('Got rotate command')
						command = param
					elif param == 200 and not command == param:
						logger.info('Got increase alt command')
						command = param
					elif param == 201 and not command == param:
						logger.info('Got decrease alt command')
						command = param
					elif param == 202 and not command == param:
						logger.info('Got increase WPNAV_SPEED command')
						command = param
					elif param == 203 and not command == param:
						logger.info('Got decrease WPNAV_SPEED command')
						command = param
					elif param == 204 and not command == param:
						logger.info('Got increase WPNAV_ACCEL command')
						command = param
					elif param == 205 and not command == param:
						logger.info('Got decrease WPNAV_ACCEL command')
						command = param
					elif param >= 0 and param < num_wp:
						# NOTE: GCS will not allow a non-existent index to be passed. The handling of negative indices is included in the conditional above for comprehension.
						logger.info('Got navigate to waypoint %d command',param)
						current_wp = int(param)
			else:
				logger.info('Not listening')
				if param == 101:
					logger.info('Got start listening command')
					listening = True
					# Set arming altitude as the desired reference altitude
					alt_initial = uav.location.global_frame.alt
					# Yaw is reported from -pi to pi with zero pointing North, so we need to convert to 0 to 360 and keep zero pointing North
					bearing = uav.attitude.yaw*180/np.pi - 180
					if bearing < 0:
						bearing = 360 + bearing
					logger.info('Rotating mission by %s degrees' %(bearing))
					uav_mission = rotate(orig_mission,bearing)
					if not bagging:
						# Start rosbag recording in a really ugly way
						bagging = True
						cmd = 'rosbag record --split --size=3000 --lz4 -a -x /camera/image -O %s' %(bagfile)
						cmd = shlex.split(cmd)
						rosbag_proc = subprocess.Popen(cmd)
						logger.info('Began rosbag in %s' % (bagfile))
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

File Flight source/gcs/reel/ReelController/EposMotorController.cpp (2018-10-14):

// JDW 2016-2-10
// Copyright Creare 2016
#include "EposMotorController.hpp"
namespace gcs {
    const unsigned short EposMotorController::NODE_ID = 1;// This would matter much more in a CAN network
    const unsigned short EposMotorController::GEAR_RATIO_INDEX = 0x2230;// The Object Index of the Gear Configuration object in EPOS memory

    EposMotorController::EposMotorController(std::string port, unsigned int baudRate) :
        portName(port), baudRate(baudRate), curOpMode(0)
    {

    }

    EposMotorController::~EposMotorController() {
        close(); // Also disables
    }

    void EposMotorController::open() 
    {
        unsigned int error_code = 0;
        
        deviceHandle = VCS_OpenDevice (
            (char*)"EPOS2",
            (char*)"MAXON SERIAL V2",
            (char*)"USB",
            (char*)portName.c_str(),
            &error_code);
            
        if(deviceHandle != 0 && error_code == 0) {
            // This get-set-get pattern lets us change just the baud rate,
            // then confirm it took.
            unsigned int actual_baud_rate = 0;
            unsigned int actual_timeout = 0;
            if(0 != VCS_GetProtocolStackSettings(deviceHandle, &actual_baud_rate, &actual_timeout, &error_code)) {
                if(0 != VCS_SetProtocolStackSettings(deviceHandle, baudRate, actual_timeout, &error_code)) {
                    if(0 != VCS_GetProtocolStackSettings(deviceHandle, &actual_baud_rate, &actual_timeout, &error_code)) {
                        if (actual_baud_rate == baudRate) {
                            // Default to a mode
                            setOperatingMode(OMD_PROFILE_POSITION_MODE);
                        } else {
                            std::stringstream ss;
                            ss << "Tried to set port rate to " << baudRate << " but instead got " << actual_baud_rate << std::endl;
                            failWithCode(ss.str(), error_code);
                        }
                    } else { failWithCode("Failed to confirm port settings", error_code); }
                } else { failWithCode("Failed to write port settings", error_code); }
            } else { failWithCode("Failed to read port settings", error_code); }
        } else { failWithCode("Failed to open motor controller", error_code); }
    }
    /************************************
                 Open/close
    ************************************/
    void EposMotorController::close() {
        disable(); // turn it off before releasing control
        
        unsigned int error_code = 0;
        if(VCS_CloseDevice(deviceHandle, &error_code) == 0)
        { failWithCode("Failed to close motor controller", error_code, false); }
    }
    void EposMotorController::clearFaultAndEnable() {
        if (isFaulted()) { clearFault(); }
        enable();
    }

    /************************************
                 State
    ************************************/
    void EposMotorController::clearFault() {
        unsigned int error_code = 0;
        if(VCS_ClearFault(deviceHandle, NODE_ID, &error_code) == 0)
        { failWithCode("Failed to clear fault", error_code); }
    }

    void EposMotorController::enable() {
        unsigned int error_code = 0;
        if(VCS_SetEnableState(deviceHandle, NODE_ID, &error_code) == 0)
        { failWithCode("Failed to set enabled state", error_code); }
    }

    void EposMotorController::disable() {
        unsigned int error_code = 0;
        if(VCS_SetDisableState(deviceHandle, NODE_ID, &error_code) == 0)
        { failWithCode("Failed to set disabled state", error_code, false); }
    }

    bool EposMotorController::isEnabled() {
        unsigned int error_code = 0;
        int enabled = 0;
        if(VCS_GetEnableState(deviceHandle, NODE_ID, &enabled, &error_code) != 0)
        {
            if(enabled) { return true; }
            else        { return false; }    
        } else { failWithCode("Failed to read fault state", error_code); return false; }
    }

    bool EposMotorController::isFaulted() {
        unsigned int error_code = 0;
        int faulted = 0;
        if(VCS_GetFaultState(deviceHandle, NODE_ID, &faulted, &error_code) != 0)
        {
            if(faulted) { return true; }
            else        { return false; }
        } else { failWithCode("Failed to read fault state", error_code); return false; }
    }
    
    
    /**
     * Gets the number of device errors.  These describe errors (if any)
     * within the motor controller device, rather than errors in the communications
     * library.  Communications library errors are thrown as std::runtime_error.
     * This is a prerequisite for calling getDeviceError() correctly.
     */
    unsigned char EposMotorController::getDeviceErrorCount() {
        unsigned int error_code = 0; // Communications library error code
        unsigned char device_error_count = 0;
        if(VCS_GetNbOfDeviceError(deviceHandle, NODE_ID, &device_error_count, &error_code) != 0)
        {
            return device_error_count;
        } else { failWithCode("Failed to read controller error count", error_code); return 0; }
    }
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

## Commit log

2013-01-01 Some print statements changed.
2013-01-01 Added symbolic links for connecting to devices on drone.
2015-02-21 Repo cleanup
    [GPS_testing_0005.csv]
2015-05-08 Adding modified dronekit class to intercept GCS messages, along with a test script. Also adding a launch script to debug this modified module. Also adding script to mount USB (for data recording).
2015-05-11 Adding test to see if we can query the Allsensors pressure transducers
2015-08-14 Added initial framework for controller
2015-09-10 Adding first cut of a basically working GUI.
2015-09-10 Controller currently runs without errors
2015-11-17 added GPSD service. Needs threading, not quite working yet.
2015-12-01 added scripts and tests
    [GPS_testing_0005.csv]
2015-12-29 Turned down the baud rate to 16kHz and got the following results:
    pi@raspberrypiGCS ~/aerowake-mit/Tests $ sudo python test_i2c_pressure_sensors.py
    Accomplished 10000 reads in 44.457492s = 4.445749ms/read = 224.933967Hz
    Accomplished 10000 interlaced reads in 44.474825s = 4.447482ms/read = 224.846304Hz
    Accomplished 10000 reads & logs in 44.927341s = 4.492734ms/read = 222.581612Hz
2015-12-29 Initial commit of pressure logging daemon. Meets 200Hz goal if baud rate is set to 512kHz or higher.
2016-01-07 Partway through adding the DLR sensors
2016-01-08 Added temperature sensor
2016-01-12 Updated to match change in temperature sensor
2016-01-19 Broke sensor readings up into two steps (reading and parsing) so that the readings can be obtained as close to simultaneous as possible. Also changed parsing to use the 3x faster struct technique.
2016-01-25 Testing Pixhawk Airspeed sensor. Different from differential pressure probes (but works the same...?) This will be used to estimating the drag on the vehicle during flight, unless we want to use the 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
2016-01-29 Turns out absolute pressure sensor's address cannot be changed.
2016-02-09 Added error handling when sensors not present
2016-02-10 Corrected full scale pressure value for .5"H20 sensor
2016-02-12 Added encoder configuration. Removed exception catching from ReelController. Added a signal handler so that killing the process will disable the motor controller via its destructor.
2016-02-12 Added tether length to motor rotation math
2016-02-21 Created and updated main.py, changed some of the foldering, and created framework for position controller.
2016-02-22 Restructured Foldering. Reel_Control under new_system/gcs/reel_control is your C++ files.
    [GPS_testing_0005.csv]
2016-02-29 Bunch of updates to the gcs and uav main loops-- will somewhat put this on hold until we have a communications protocol inplace for the raspberry pi to raspberry pi connection. Next will be unit test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
2016-04-07 This successfully opens and reads from the EPOS motor controller
2016-04-07 The motor twitches and moves by one encoder tick, no matter how big a delta it's commanded. I'm pretty sure the encoder settings are being communicated incorrectly.
2016-04-08 Motor moves now. Turns out I was destructing the RellController object prior to waiting, which disabled the motor immediately after commanding movement.
2016-04-15 Backup commit: partially working, moves 11cm when 10cm are commanded. Added tether length command to commandline. Removed application of encoder settings on startup
2016-04-18 Revert "Repo cleanup"
    This reverts commit 226aa2f956e5eede026b738e2c364767b94de205.
    [GPS_testing_0005.csv]
2016-04-19 modified parameter values and converstion equation for the DLVR differential pressure sensors
2016-04-28 Copying this from /Logging/sensors. Next cleanup, we might want to consider making one main "sensors" package.
2016-05-02 Updated cartesian controller to log state information. Battery state logging works.
2016-05-04 First draft tension sensor reader script
2016-05-09 With the current design, it seems more prudent to leave the profile set in place
2016-05-09 Created mock tension sensor and reel controller for testing without full hardware
2016-05-13 May not compile - first draft of changing the cython boundary from the middle of reel control to the motor control
2016-05-13 Changed mock reel controller to a mock motor controller, moved reel-related functionality from ReelController.cpp to ReelController.py
2016-05-19 Added debug prints
2016-05-20 The motor controller, it turns out, will lower the profile velocity to match the velocity commanded by the setMaxVelocity command, and will reject commands to raise the velocity above that value. Upd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
2016-05-20 Motor controller rejects profile RPM < 1; added check for that.
2016-05-24 Changed exceptions to include error message rather than printing to stdout. Also added getMaxAccelDecel()
2016-05-26 UAV push working configuration
    [uav_log_file_1464285304.csv, uav_log_file_1464287559.csv, uav_log_file_1464288521.csv, uav_log_file_1464289932.csv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]
2016-08-09 Fixed cross-thread issue with the ReelController object
2017-01-26 Reorganized. Don't need "old_system", and "new_system" is misleading.
    [GPS_testing_0005.csv, uav_log_file_1464285304.csv, uav_log_file_1464287559.csv, uav_log_file_1464288521.csv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]
2017-01-27 Added mock versions of the sensors on the air probe
2017-01-27 Began integration of airprobe sensor logger into main application
2017-01-27 +mock sensor file
2017-01-31 Now logs pressures from mock probe sensors
2017-02-17 Clarified printouts
2017-02-23 Finished adding status display framework to the GCS. Also cleaned up "quit" button so the [x] on the window does the same thing. Doesn't always cleanly exit.
2017-10-12 Empty commit to make the timeline look cleaner. The last few commits were on a raspberry Pi where the date wasn't set right, so while they appear to be from 2016, they were actually from earlier this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
2017-10-13 The entire "object dictionary" of EPOS motor control settings, as I found it today.
2017-10-18 Reel case BOM and update to HW interconnect diagram
    [ReelCaseBOM.xlsx]
2017-10-20 Added critical OS files from the Pi. If these settings aren't applied (specifically the device tree overlays), the bluetoth module will be internally connected to the same port as the PixHawk, and th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
2017-10-27 Flight ready. Removed multiple debugging lines. Removed multiple unused functions. Commented out arming of uav. Changed control loop conditional statement to test for mode guided in addition to gcs a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
2017-10-27 Set maximum attitude to 15 degrees instead of 30 degrees. Commented out some debugging printouts.
2017-11-30 Working on threading the read_mission() function so it does not cause control loop to wait.
2017-12-01 Added threading. Reading the mission from the gcs now occurs in a separate thread. An intermediate variable acts as a message carrier between the main (control loop) thread and the mission reader thr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
2017-12-01 Working on threading.
2017-12-18 Added Bill of Materials for MIT side of project.
    [mit_bom.xlsx]
2017-12-18 Adding MIT Bill of Materials to master.
    [mit_bom.xlsx]
2018-01-02 Added optical filter to mit_bom.xlsx
    [mit_bom.xlsx]
2018-01-11 my_main.py tests an alternative uav controller. Currently relies on SITL.
2018-01-19 NOT FLIGHT READY. Testing thread death issue.
2018-01-19 Muted some print statements.
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2018-07-02 Debugged reel in my_main.py. Slight bug still exists where reel will go to power on position whenever the script begins.
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2018-07-16 defined a local mission, changed everything that said heading to bearing, changed implementation of rotating mission to work correctly
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2018-07-30 set initial bearing to 0, added check/fix to keep new_bearing within constraints of rotate_mission
2018-07-30 moved mission rotation to where rest of command handling is in code, set initial bearing to 0, fixed repeated rotate command problem
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2018-09-04 The __init__.py file belongs in /usr/local/lib/python2.7/dist-packages/dronekit/ . It has been modified to ignore 'timeout setting parameter ...' messages since those messages have never been true in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
2018-10-02 Fixed mock motor controller's faulted state
2018-10-03 Commiting changes made by John to make sensors read from correct bus.
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2018-10-04 Added some tolerance to motor controller communication exceptions. Still need to test this with the real motor controller.
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2018-10-04 Uncommented status logging. Fixed initialization of reel motor controller.
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2018-10-10 Fixed cp /tmp command. Also fixed ROSBAGLOGNAMES echo. Also stopped printing to screen if no logs exist.
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2018-10-11 Draft of device error lookup. Haven't yet tried to compile.
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2018-10-11 Missed a return statement. Getting and setting uint16 objects with the actual motor controller appears to work. Getting a list of errors from a non-faulted motor controller results in an empty list -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
2018-10-14 Added printout for new target alt whenever GCS operator commands altitude change. Fixed whitespace for clearfault commands. Finally, added ability to change reel position in increments by increasing 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
